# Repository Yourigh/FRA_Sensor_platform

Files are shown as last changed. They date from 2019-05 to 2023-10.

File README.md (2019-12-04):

# FRA Sensor platform
Analog and Digital datalogger with 16 analog channels (16bit) with programmable gain amplifier (auto ranged from 0-256mV to 0-5V).

# Main board picture
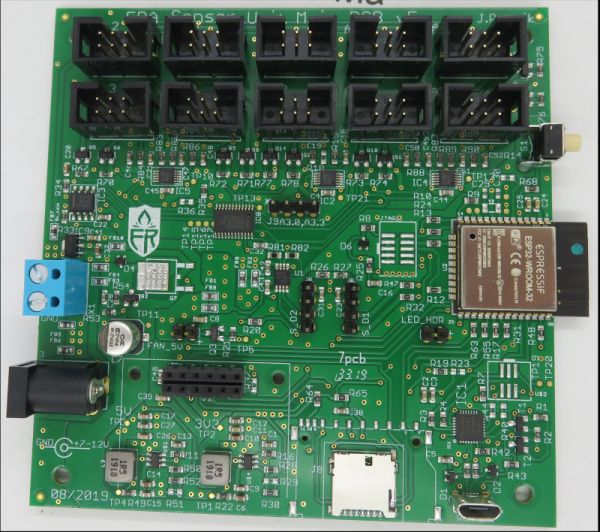
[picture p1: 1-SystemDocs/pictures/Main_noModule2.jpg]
Assembled main board

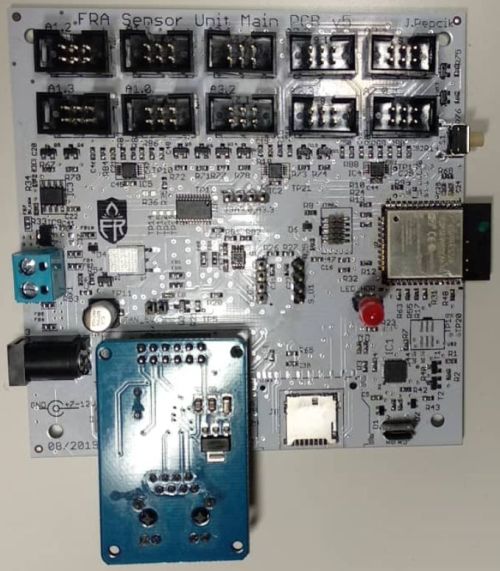
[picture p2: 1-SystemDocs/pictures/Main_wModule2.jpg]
Assembled main board with Ethernet controller


# Development tools
Built on ESP32 module and Arduino framework using Platformio IDE.

# Firmware download to ESP32
https://www.espressif.com/en/products/hardware/esp32/resources

Tools -> Flash Download Tool

Built binary files with the guide are located here:

https://github.com/Yourigh/FRA_Sensor_platform/tree/master/3-FW_SW/1-FW_device/Programming_procedure

Update the esptool.py to newest from:

https://github.com/espressif/esptool

# Resources
https://github.com/greiman/SdFat

https://github.com/jrowberg/i2cdevlib/tree/master/Arduino/ADS1115

https://github.com/8-DK/EtherCard

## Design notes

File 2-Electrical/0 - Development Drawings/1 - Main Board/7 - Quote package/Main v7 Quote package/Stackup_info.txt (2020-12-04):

Board Size: 100x100mm
stackup thickness: 1.6mm
2 layers
single side SMT assembly + single side TH assembly
Legend (silkscreen) - only from TOP side
HAL surface is OK.

Chnage list:
V3.2	original version
V4.1	C19 changed to DNI
V5	D1,D2,D4,D6 package fixed to SC70 (was SOT23)
V7	Changed footprint of ESP32-WROOM-32 to ESP32-WROOM-32E

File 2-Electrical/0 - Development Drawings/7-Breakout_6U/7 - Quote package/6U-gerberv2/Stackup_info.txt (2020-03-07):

Board Size: 51x67mm
stackup thickness: 1.6mm
2 layers
double side TH assembly
HAL surface is OK.

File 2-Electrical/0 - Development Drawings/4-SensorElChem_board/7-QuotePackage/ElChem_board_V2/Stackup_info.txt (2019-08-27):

Board Size: 22x55mm
stackup thickness: 1.6mm
2 layers
single side SMT assembly + single side TH assembly from TOP side
Legend (silkscreen) - both sides

Chnage list:
V1	initial version
V2	Gerber route change (RE and CE on sensor miswired), placment and BOM stays the same

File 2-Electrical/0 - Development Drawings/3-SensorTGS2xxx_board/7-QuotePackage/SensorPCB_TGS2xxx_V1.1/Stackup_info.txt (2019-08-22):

Board Size: 20x30mm
stackup thickness: 1.6mm
2 layers
single side SMT assembly + single side TH assembly from TOP side
Legend (silkscreen) - both sides

Chnage list:
V1	initial version
V1.1	C13 changed from 100n to 1n - only BOM change (affects only variant B)

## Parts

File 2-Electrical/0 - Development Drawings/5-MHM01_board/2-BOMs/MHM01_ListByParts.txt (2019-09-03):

Part	Value	Attributes	Package	Description	Part Num
C1	10u		C1206	CAPACITOR, European symbol	JMF316AB7106KLHT
C2	10u		C1206	CAPACITOR, European symbol	JMF316AB7106KLHT
C3	1u		C0603K	CAPACITOR, European symbol	GRM188R71C105KE15D
C5	10u		C0603K	CAPACITOR, European symbol	GRM188R61A106KE69J
C7	100n		C0603K	CAPACITOR, European symbol	CC0603KRX7R8BB104
FB1			0603	Ferrite Bead	BLM18PG121SN1D
FID1	FIDUCIAL""		FIDUCIAL_1MM	Fiducial Alignment Points	*
FID2	FIDUCIAL""		FIDUCIAL_1MM	Fiducial Alignment Points	*
FID4	FIDUCIAL""		FIDUCIAL_1MM	Fiducial Alignment Points	*
LED2	Red		CHIPLED_1206	LED	BR1101W-TR
PS1	AP2202K-ADJTRG1		SOT95P280X145-5N	DiodesZetex AP2202K-ADJTRG1, Low Noise LDO Voltage Regulator, Adjustable 150mA, 2.3  13.2 V +/-2%, 5-Pin SOT-23	AP2202K-ADJTRG1
Q1	Si2300DS		SOT23	N-Channel Mosfet	JMF316AB7106KLHT
R1	75		R1206	RESISTOR, European symbol	CRCW120675R0FKEA
R2	10k		R0603	RESISTOR, European symbol	CRCW060310K0FKEA
R3	3k		R0603	RESISTOR, European symbol	ERA-3AEB302V
R4	0		R1206	RESISTOR, European symbol	CRCW12060000Z0EA
R7	75		R1206	RESISTOR, European symbol	CRCW120675R0FKEA
R8	10k		R0603	RESISTOR, European symbol	CRCW060310K0FKEA
R9	220		R0603	RESISTOR, European symbol	CRCW0603220RFKEA
R12	100		RJ9W	POTENTIOMETER	3296X-1-101LF
R19	DNI		R1206	RESISTOR, European symbol	*
R20	75		R1206	RESISTOR, European symbol	CRCW120675R0FKEA
R21	75		R1206	RESISTOR, European symbol	CRCW120675R0FKEA
R22	10K		R1206	RESISTOR, European symbol	CRCW120610K0FKEA
TP1	TPTP10R		TP10R	Test pad	*
TP2	TPTP10R		TP10R	Test pad	*
TP6	TPTP10R		TP10R	Test pad	*
TP7	TPTP10R		TP10R	Test pad	*
U$1	CONN_03X2_WE_61200621621		WE_61200621621	https://eu.mouser.com/ProductDetail/Wurth-Elektronik/61200621621?qs=sGAEpiMZZMs%252BGHln7q6pm%2FFhW%252BtWvhAgbNxkR%252BlwXp8Ip%2FAN9J9VOg%3D%3D	61200621621
U2	FIGARO_SR-7		FIGARO-SR7		SR-7
X1	TB001-500-02BE		W237-102	WAGO SCREW CLAMP	TB001-500-02BE
X2	TB001-500-02BE		W237-102	WAGO SCREW CLAMP	TB001-500-02BE
X3	TB001-500-02BE		W237-102	WAGO SCREW CLAMP	TB001-500-02BE

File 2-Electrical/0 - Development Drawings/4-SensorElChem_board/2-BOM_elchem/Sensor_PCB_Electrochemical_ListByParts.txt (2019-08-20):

Part	Value	Attributes	Package	Description	Part Num
C1	DNI		C0603K	CAPACITOR, European symbol	*
C2	100n		C0603K	CAPACITOR, European symbol	GRM188R71C104KA01D
C8	100n		C0603K	CAPACITOR, European symbol	GRM188R71C104KA01D
C9	100n		C0603K	CAPACITOR, European symbol	GRM188R71C104KA01D
C12	100n		C0603K	CAPACITOR, European symbol	GRM188R71C104KA01D
FB9			0603	Ferrite Bead	BLM18PG121SN1D
FID3	FIDUCIAL1X1UNMASKED		FIDUCIAL_1MM_UNMASKED	Fiducial Alignment Points	*
FID5	FIDUCIAL1X1UNMASKED		FIDUCIAL_1MM_UNMASKED	Fiducial Alignment Points	*
FID6	FIDUCIAL1X1UNMASKED		FIDUCIAL_1MM_UNMASKED	Fiducial Alignment Points	*
FID7	FIDUCIAL1X1UNMASKED		FIDUCIAL_1MM_UNMASKED	Fiducial Alignment Points	*
FID8	FIDUCIAL1X1UNMASKED		FIDUCIAL_1MM_UNMASKED	Fiducial Alignment Points	*
FID9	FIDUCIAL1X1UNMASKED		FIDUCIAL_1MM_UNMASKED	Fiducial Alignment Points	*
IC4	LMP91000SD_NOPB		SON50P400X400X80-15N	Configurable AFE Potentiostat for Low-Power Chemical Sensing Applications	LMP91000
IC5	REF3125AQDBZRQ1		SOT95P237X112-3N	Automotive 20-ppm/C (max), 100-A, 3-pin SOT-23 series voltage reference	REF3125AQDBZRQ1
J1	CONN_03X2_WE_61200621621		WE_61200621621	https://eu.mouser.com/ProductDetail/Wurth-Elektronik/61200621621?qs=sGAEpiMZZMs%252BGHln7q6pm%2FFhW%252BtWvhAgbNxkR%252BlwXp8Ip%2FAN9J9VOg%3D%3D	30306-6002HB
J2	2wire		1X02	PIN HEADER	TSW-102-07-G-S
JP2	JUMPER-SMT_3_NO_NO_SILK		SMT-JUMPER_3_0-NO_TRACE_NO-SILK	Normally open jumper	*
LED1			CHIP-LED0603	LED	IN-S63AT5G
Q1	PMBFJ177,215		SOT95P230X110-3N	NXP PMBFJ177,215 P-channel JFET Transistor, 30 V, Idss 1.5  20mA, 3-Pin SOT-23	PMBFJ177,215
R12	10		R0603	RESISTOR, European symbol	CRCW060310R0FKEA
R20	10k		R0603	RESISTOR, European symbol	CRCW060310K0FKEA
R21	10k		R0603	RESISTOR, European symbol	CRCW060310K0FKEA
R22	0		R0603	RESISTOR, European symbol	CRCW06030000Z0EA
R24	100		R0603	RESISTOR, European symbol	CRCW0603100RFKEA
U2	TGS5042		TGS5042	TGS5042	INSTALLED_BY_CUSTOMER
X1	3-ELECTRODE-GAS-SENSOR_SOCKET		3-ELE_SOCKET_ANDON	3 electrode electrochemical sensors	INSTALLED_BY_CUSTOMER

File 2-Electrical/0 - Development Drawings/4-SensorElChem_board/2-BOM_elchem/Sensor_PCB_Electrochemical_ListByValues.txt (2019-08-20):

Qty	Value	Part Num	Package	Parts
1		BLM18PG121SN1D	0603	FB9
1		IN-S63AT5G	CHIP-LED0603	LED1
1	0	CRCW06030000Z0EA	R0603	R22
1	2wire	TSW-102-07-G-S	1X02	J2
1	3-ELECTRODE-GAS-SENSOR_SOCKET	INSTALLED_BY_CUSTOMER	3-ELE_SOCKET_ANDON	X1
1	10	CRCW060310R0FKEA	R0603	R12
2	10k	CRCW060310K0FKEA	R0603	R20, R21
1	100	CRCW0603100RFKEA	R0603	R24
4	100n	GRM188R71C104KA01D	C0603K	C2, C8, C9, C12
1	CONN_03X2_WE_61200621621	30306-6002HB	WE_61200621621	J1
1	DNI	*	C0603K	C1
6	FIDUCIAL1X1UNMASKED	*	FIDUCIAL_1MM_UNMASKED	FID3, FID5, FID6, FID7, FID8, FID9
1	JUMPER-SMT_3_NO_NO_SILK	*	SMT-JUMPER_3_0-NO_TRACE_NO-SILK	JP2
1	LMP91000SD_NOPB	LMP91000	SON50P400X400X80-15N	IC4
1	PMBFJ177,215	PMBFJ177,215	SOT95P230X110-3N	Q1
1	REF3125AQDBZRQ1	REF3125AQDBZRQ1	SOT95P237X112-3N	IC5
1	TGS5042	INSTALLED_BY_CUSTOMER	TGS5042	U2

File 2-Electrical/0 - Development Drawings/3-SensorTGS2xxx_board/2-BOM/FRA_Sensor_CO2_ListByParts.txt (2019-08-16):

Part	Value	Attributes	Package	Description	Part Num
C1(DNP)	100n		C0603K	CAPACITOR, European symbol	GRM188R71C104KA01D
C2	100n		C0603K	CAPACITOR, European symbol	GRM188R71C104KA01D
C3	100n		C0603K	CAPACITOR, European symbol	GRM188R71C104KA01D
C9	100n		C0603K	CAPACITOR, European symbol	GRM188R71H102KA01D
C10(DNP)	1n		C0603K	CAPACITOR, European symbol	GRM188R71H102KA01D
C13(DNP)	100n		C0603K	CAPACITOR, European symbol	GRM188R71C104KA01D
FB1(DNP)			0603	Ferrite Bead	BLM18PG121SN1D
FB9			0603	Ferrite Bead	BLM18PG121SN1D
FID1	FIDUCIAL""		FIDUCIAL_1MM	Fiducial Alignment Points	*
FID2	FIDUCIAL""		FIDUCIAL_1MM	Fiducial Alignment Points	*
FID4	FIDUCIAL""		FIDUCIAL_1MM	Fiducial Alignment Points	*
IC3	LMV796MF_NOPB		SOT95P280X145-5N	Single 17 MHz, low noise, CMOS input, 1.8V operational amplifier	LMV796MF
IC6(DNP)	MCP6541T-I_OT		SOT95P270X145-5N	Comparator Push-Pull RRIO 1.6V SOT23-5	MCP6541T-I/OT
J1	CONN_03X2		WE_61200621621	https://eu.mouser.com/ProductDetail/Wurth-Elektronik/61200621621?qs=sGAEpiMZZMs%252BGHln7q6pm%2FFhW%252BtWvhAgbNxkR%252BlwXp8Ip%2FAN9J9VOg%3D%3D	30306-6002HB
Q3(DNP)	Si2300DS		SOT23	N-Channel Mosfet	SI2300DS-T1-GE3
R1(DNP)	100k		R0603	RESISTOR, European symbol	CRCW0603100KFKEA
R2(DNP)	0		R0603	RESISTOR, European symbol	CRCW06030000Z0EA
R3	0		R0603	RESISTOR, European symbol	CRCW06030000Z0EA
R4	0		R0603	RESISTOR, European symbol	CRCW06035K10FKEA
R10(DNP)	10		R0603	RESISTOR, European symbol	CRCW060310R0FKEA
R11	10		R0603	RESISTOR, European symbol	CRCW060310R0FKEA
R13	0		R0603	RESISTOR, European symbol	CRCW06030000Z0EA
R19	10k		R0603	RESISTOR, European symbol	CRCW060310K0FKEA
R23	0		R0603	RESISTOR, European symbol	CRCW06030000Z0EA
R25(DNP)	100k		R0603	RESISTOR, European symbol	CRCW0603100KFKEA
R26(DNP)	5.1k		R0603	RESISTOR, European symbol	CRCW06035K10FKEA
R27(DNP)	100k		R0603	RESISTOR, European symbol	CRCW0603100KFKEA
U2	FIGARO_SR-7		FIGARO-SR7		INSTALLED_BY_CUSTOMER

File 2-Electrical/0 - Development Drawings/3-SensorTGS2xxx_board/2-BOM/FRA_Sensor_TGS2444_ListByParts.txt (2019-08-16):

Part	Value	Attributes	Package	Description	Part Num
C1(DNP)	100n		C0603K	CAPACITOR, European symbol	GRM188R71C104KA01D
C2	100n		C0603K	CAPACITOR, European symbol	GRM188R71C104KA01D
C3	100n		C0603K	CAPACITOR, European symbol	GRM188R71C104KA01D
C9	1n		C0603K	CAPACITOR, European symbol	GRM188R71H102KA01D
C10	1n		C0603K	CAPACITOR, European symbol	GRM188R71H102KA01D
C13	100n		C0603K	CAPACITOR, European symbol	GRM188R71C104KA01D
FB1			0603	Ferrite Bead	BLM18PG121SN1D
FB9			0603	Ferrite Bead	BLM18PG121SN1D
FID1	FIDUCIAL""		FIDUCIAL_1MM	Fiducial Alignment Points	*
FID2	FIDUCIAL""		FIDUCIAL_1MM	Fiducial Alignment Points	*
FID4	FIDUCIAL""		FIDUCIAL_1MM	Fiducial Alignment Points	*
IC3(DNP)	LMV796MF_NOPB		SOT95P280X145-5N	Single 17 MHz, low noise, CMOS input, 1.8V operational amplifier	LMV796MF
IC6	MCP6541T-I_OT		SOT95P270X145-5N	Comparator Push-Pull RRIO 1.6V SOT23-5	MCP6541T-I/OT
J1	CONN_03X2		WE_61200621621	https://eu.mouser.com/ProductDetail/Wurth-Elektronik/61200621621?qs=sGAEpiMZZMs%252BGHln7q6pm%2FFhW%252BtWvhAgbNxkR%252BlwXp8Ip%2FAN9J9VOg%3D%3D	30306-6002HB
Q3	Si2300DS		SOT23	N-Channel Mosfet	SI2300DS-T1-GE3
R1	100k		R0603	RESISTOR, European symbol	CRCW0603100KFKEA
R2	0		R0603	RESISTOR, European symbol	CRCW06030000Z0EA
R3(DNP)	0		R0603	RESISTOR, European symbol	CRCW06030000Z0EA
R4	5.1k		R0603	RESISTOR, European symbol	CRCW06035K10FKEA
R10	10		R0603	RESISTOR, European symbol	CRCW060310R0FKEA
R11(DNP)	10		R0603	RESISTOR, European symbol	CRCW060310R0FKEA
R13(DNP)	0		R0603	RESISTOR, European symbol	CRCW06030000Z0EA
R19	10k		R0603	RESISTOR, European symbol	CRCW060310K0FKEA
R23(DNP)	0		R0603	RESISTOR, European symbol	CRCW06030000Z0EA
R25	100k		R0603	RESISTOR, European symbol	CRCW0603100KFKEA
R26	5.1k		R0603	RESISTOR, European symbol	CRCW06035K10FKEA
R27	100k		R0603	RESISTOR, European symbol	CRCW0603100KFKEA
U2	FIGARO_SR-7		FIGARO-SR7		INSTALLED_BY_CUSTOMER

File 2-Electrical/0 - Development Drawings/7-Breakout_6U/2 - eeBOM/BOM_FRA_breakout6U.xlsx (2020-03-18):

Qty | Value | MPN | Parts | Mouser
6 | 2x3pin female | SSW-103-01-F-D | U5,U6,U7,U8,U9,U10 | https://www.mouser.com/ProductDetail/Samtec/SSW-103-01-F-D
2 | Terminal 10p vertical | TB003V-500-P10BE | U12,U14 | https://www.mouser.com/ProductDetail/CUI-Devices/TB003V-500-P10BE

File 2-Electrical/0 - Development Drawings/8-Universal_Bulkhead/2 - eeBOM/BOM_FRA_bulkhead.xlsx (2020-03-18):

Qty | Value | MPN | Parts | Mouser
2 | 2pin male | TSW-102-07-G-S | FAN_5V, LED_HDR | https://www.mouser.com/ProductDetail/Samtec/TSW-102-07-G-S
1 | 2pin female | SLW-102-01-T-S | LED_HDR1 | https://www.mouser.com/ProductDetail/Samtec/SLW-102-01-T-S
2 | 4pin male | TSW-104-07-G-S | J9, S_D1 | https://www.mouser.com/ProductDetail/Samtec/TSW-104-07-G-S?qs=sGAEpiMZZMvlX3nhDDO4AAakfwUUEeIPjXtR1hQiW00%3D
2 | 4pin female | SLW-104-01-T-S | S_D2, S_D3 | https://www.mouser.com/ProductDetail/Samtec/SLW-104-01-T-S
20 | 2x3pin male | Wurth 61200621621 | U$1, U$2, U$3, U$4, U$5, U$6, U$8, U$9, U$10, U$11, U$12, U$1 3, U$14, U $15, U$16, U$17, U$18, U$19, U$20, U$21 | https://eu.mouser.com/ProductDetail/Wurth-Elektronik/61200621621
1 | Terminal 2p | TB001-500-02BE | X1 | https://www.mouser.com/ProductDetail/CUI-Devices/TB001-500-02BE
3 | Terminal 5p | TB003-500-P05BE | U1, U3, U22 | https://www.mouser.com/ProductDetail/CUI-Devices/TB003-500-P05BE
2 | Terminal 10p | TB003-500-P10BE | U2, U23 | https://www.mouser.com/ProductDetail/CUI-Devices/TB003-500-P10BE

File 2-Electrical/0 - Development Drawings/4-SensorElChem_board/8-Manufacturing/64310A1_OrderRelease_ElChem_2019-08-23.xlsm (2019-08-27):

 |  |  |  | Production Order Description
 |  |  |  | Number: Q64310A1 |  |  |  |  | Issued by: |  | Eyoel
 |  |  |  |  | 2019-08-23 |  |  |  | Ver: 01
General Information |  |  |  | Project Co-odinator |  |  |  |  | Twinkle
1.Project Name: | ElChem_V1 |  |  |  |  |  |  |  |  | 7.Ordered Date: |  |  | 2019-08-23
2.Gerber received date: | ElChem_V1_2019_08_20 |  |  |  |  |  |  |  |  | 8.Customer ID: |  |  | 52940
3.DFM Check: | Yes |  |  |  |  |  |  |  |  | 9.Repeated order: |  |  | No
4.PCBA Shipment | 1st | 225 | 2nd | 0 | 3rd |  | 4th |  |  | 10.PCBA Ordered: |  |  | 225 | PCS
5.Bare PCB shipmt | 1st | 0 | 2nd | 0 | 3rd |  | 4th |  |  | 11.Customer PO |  |  | 997-007
6.Shipment date: | 2019-09-09 |  |  |  |  |  |  |  |  | 11a. Type of Service |  |  | Turnkey
BOM and Parts Procurement:
12.BOM received Date: | 2019-08-19 |  |  |  |  |  |  |  |  | 15.SZ stock check: |  |  | No
13.Consigned Parts: | None |  |  |  |  |  |  |  |  | 16.Authoriz Code: |  |  | 8279010823
14.DNI Parts: | Item # 3,5,9a,11,12,15,16 |  |  |  |  |  |  |  |  | 17.Parts procurement: |  |  | Geoffrey |  |  | # of days required for Purchasing | 3
17a. Procurement finish Date | 2019-08-26 |  |  |  |  |  |  |  |  | 17b. Parts arrival in Toronto |  |  | 2019-08-27
 |  |  |  |  |  |  |  |  |  |  |  |  |  |  |  | Note: These days are not for rush orders
Special Assembly Requirements: |  |  |  |  |  |  |  |  |  | 18.Assembly Process |  |  | Lead-free
Please process as a rush order as the client has paid extra for it. Please fabricate all the boards by August 30th, parts should arrive by then.
Please assemble as soon as possible and send out by September 9th.
Process In Markham.
19.Returning Parts: | None |  |  | 24.Conformal Coating: |  |  |  | No |  |  | 28.SMT Pads |  | 45
 |  |  |  |  |  |  |  |  |  |  | 29. Holes |  | 10
20.Picture Approval: | Yes |  |  | 25.Programming: |  |  |  | No |  |  | 30. BOM Lines |  | 17
 |  |  |  |  |  |  |  |  |  |  | 31. All Parts |  | 14
21.Functional Testing: | No |  |  | 26.Shipped by: |  |  |  | UPS/FedEx |  |  | 32. Double side |  | N
 |  |  |  |  |  |  |  |  |  |  | 33. Leadfree |  | Y
22.Files Provided: | Gerber files, ProductionBOM |  |  |  |  |  |  |  |  |  | 34. BGA/Fine Pitch |  | 0
 |  |  |  |  |  |  |  |  |  |  | 35. Package |  | 0603
23.Parts for Approval: | None |  |  | 27. Balance Payment: |  |  |  | - |  |  | 37. BGA/QFN |  | 0 | 0 | 0.00
 |  |  |  |  |  |  |  |  |  |  | 38. Fine Pitch |  | 0 | 0 | 0.00
PCB fab notes: |  | 1st order: |  | 225 | PCS |  |  |  | 2nd order: |  | 0 | PCS
Other requirements: Please process as a rush order as the client has paid extra for it. Please fabricate all the boards by August 30th, parts should arrive by then.
Please assemble as soon as possible and send out by September 9th.
Board Size: | 0.86 |  | inch | X | 2.16 | inch |  |  | Impedance Control: |  |  |  | NO
Panel Size: |  |  | inch | X |  | inch |  |  | Materials: |  |  | FR4(TG140)
Board Thickness: | 0.063 |  | inch |  |  |  |  |  | No. of Layers: |  |  | 2
Legend Color: | White |  |  | 2 | Sides |  |  |  | Mask Color: |  |  | Green |  | 2 | Sides
Copper Weight: | Outer 1.0/1.0 oz |  |  |  |  |  |  |  | Electrical Testing: |  |  |  | YES
Panelization: |  |  |  | 1PNL | = |  | pcs. |  | Surface Finish: |  |  | Gold Immersion
Blind or Buried vias: |  | NO |  |  |  |  |  |  | Gold finger: |  |  |  | NO
 |  |  |  |  |  |  |  |  | Via on Pad: |  |  | NO

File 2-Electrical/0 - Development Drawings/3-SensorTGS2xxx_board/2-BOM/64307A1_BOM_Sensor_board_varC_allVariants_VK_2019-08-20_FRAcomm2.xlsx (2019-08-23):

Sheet: varA
Variant A - TGS2xxx
Assembly:
Part | Value | Package | Description | Part Num | X [mm] | Y [mm] | Orientation
C1 | 100n | C0603K | CAPACITOR, European symbol | GRM188R71C104KA01D | 15.355 | 28.544 | R180
C2 | 100n | C0603K | CAPACITOR, European symbol | GRM188R71C104KA01D | 8.385 | 11.022 | R0
FB1 |  | 603 | Ferrite Bead | BLM18PG121SN1D | 11.22 | 17.452 | R180
FB9 |  | 603 | Ferrite Bead | BLM18PG121SN1D | 10.409 | 13.299 | R0
FID1 | FIDUCIAL"" | FIDUCIAL_1MM | Fiducial Alignment Points | * | 14.59 | 1.355 | R0
FID2 | FIDUCIAL"" | FIDUCIAL_1MM | Fiducial Alignment Points | * | 3.11 | 24.92 | R0
FID4 | FIDUCIAL"" | FIDUCIAL_1MM | Fiducial Alignment Points | * | 18.925 | 28.94 | R0
J1 | CONN_03X2 | WE_61200621621 | Pin header connector | 30306-6002HB | 7.136 | 5.278 | R270
R2 | 0 | R0603 | RESISTOR, European symbol | CRCW06030000Z0EA | 10.035 | 24.885 | R90
R4 | 5.1k | R0603 | RESISTOR, European symbol | CRCW06035K10FKEA | 18.535 | 18.734 | R270
R10 | 10 | R0603 | RESISTOR, European symbol | CRCW060310R0FKEA | 18.038 | 6.487 | R270
R23 | 0 | R0603 | RESISTOR, European symbol | CRCW06030000Z0EA | 18.569 | 14.186 | R270
Procurement:
Qty | Value | Part Num | Package | Parts | Alternative
2 |  | BLM18PG121SN1D | 603 | FB1, FB9
2 | 0 | CRCW06030000Z0EA | R0603 | R2, R3(DNP), R13(DNP), R23
0 | 1n | GRM188R71H102KA01D | C0603K | C9(DNP), C10(DNP)
1 | 5.1k | CRCW06035K10FKEA | R0603 | R4, R26(DNP)
1 | 10 | CRCW060310R0FKEA | R0603 | R10, R11(DNP)
0 | 10k | CRCW060310K0FKEA | R0603 | R19(DNP)
0 | 100k | CRCW0603100KFKEA | R0603 | R1(DNP), R25(DNP), R27(DNP)
2 | 100n | GRM188R71C104KA01D | C0603K | C1, C2, C3(DNP), C13(DNP)
1 | CONN_03X2 | 30306-6002HB |  | J1 | Wurth 61200621621
0 | LMV796MF_NOPB | LMV796MF | SOT95P280X145-5N | IC3(DNP)
0 | MCP6541T-I_OT | MCP6541T-I/OT | SOT95P270X145-5N | IC6(DNP)
0 | Si2300DS | SI2300DS-T1-GE3 | SOT23 | Q3(DNP)

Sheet: varB
Variant B - TGS2444
Assembly:
Part | Value | Attributes | Package | Description | Part Num | X [mm] | Y [mm] | Orientation
C2 | 100n |  | C0603K | CAPACITOR, European symbol | GRM188R71C104KA01D | 8.385 | 11.022 | R0
C3 | 100n |  | C0603K | CAPACITOR, European symbol | GRM188R71C104KA01D | 2.115 | 23.265 | R0
C9 | 1n |  | C0603K | CAPACITOR, European symbol | GRM188R71H102KA01D | 12.417 | 11.033 | R180
C10 | 1n |  | C0603K | CAPACITOR, European symbol | GRM188R71H102KA01D | 3.983 | 12.292 | R270
C13 | 100n |  | C0603K | CAPACITOR, European symbol | GRM188R71C104KA01D | 15.75 | 12.555 | R0
FB1 |  |  | 603 | Ferrite Bead | BLM18PG121SN1D | 11.22 | 17.452 | R180
FB9 |  |  | 603 | Ferrite Bead | BLM18PG121SN1D | 10.409 | 13.299 | R0
FID1 | FIDUCIAL"" |  | FIDUCIAL_1MM | Fiducial Alignment Points | * | 14.59 | 1.355 | R0
FID2 | FIDUCIAL"" |  | FIDUCIAL_1MM | Fiducial Alignment Points | * | 3.11 | 24.92 | R0
FID4 | FIDUCIAL"" |  | FIDUCIAL_1MM | Fiducial Alignment Points | * | 18.925 | 28.94 | R0
IC6 | MCP6541T-I_OT |  | SOT95P270X145-5N | Comparator Push-Pull RRIO 1.6V SOT23-5 | MCP6541T-I/OT | 4.277 | 17.317 | R270
J1 | CONN_03X2 |  | WE_61200621621 | https://eu.mouser.com/ProductDetail/Wurth-Elektronik/61200621621 | 30306-6002HB | 7.136 | 5.278 | R270
Q3 | Si2300DS |  | SOT23 | N-Channel Mosfet | SI2300DS-T1-GE3 | 15.754 | 15.895 | R0
R1 | 100k |  | R0603 | RESISTOR, European symbol | CRCW0603100KFKEA | 6.738 | 21.313 | R180
R2 | 0 |  | R0603 | RESISTOR, European symbol | CRCW06030000Z0EA | 10.035 | 24.885 | R90
R4 | 5.1k |  | R0603 | RESISTOR, European symbol | CRCW06035K10FKEA | 18.535 | 18.734 | R270
R10 | 10 |  | R0603 | RESISTOR, European symbol | CRCW060310R0FKEA | 18.038 | 6.487 | R270
R19 | 10k |  | R0603 | RESISTOR, European symbol | CRCW060310K0FKEA | 7.695 | 18.405 | R90
R25 | 100k |  | R0603 | RESISTOR, European symbol | CRCW0603100KFKEA | 1.724 | 12.329 | R90
R26 | 5.1k |  | R0603 | RESISTOR, European symbol | CRCW06035K10FKEA | 1.184 | 17.285 | R90
R27 | 100k |  | R0603 | RESISTOR, European symbol | CRCW0603100KFKEA | 2.076 | 20.731 | R0
Procurement:
Qty | Value | Part Num | Package | Parts | Alternative
2 |  | BLM18PG121SN1D | 603 | FB1, FB9
1 | 0 | CRCW06030000Z0EA | R0603 | R2, R3(DNP), R13(DNP), R23(DNP)
2 | 1n | GRM188R71H102KA01D | C0603K | C9, C10
2 | 5.1k | CRCW06035K10FKEA | R0603 | R4, R26
1 | 10 | CRCW060310R0FKEA | R0603 | R10, R11(DNP)
1 | 10k | CRCW060310K0FKEA | R0603 | R19
3 | 100k | CRCW0603100KFKEA | R0603 | R1, R25, R27
3 | 100n | GRM188R71C104KA01D | C0603K | C1(DNP), C2, C3, C13
1 | CONN_03X2 | 30306-6002HB |  | J1 | Wurth 61200621621
1 | FIGARO_SR-7 | INSTALLED_BY_CUSTOMER | FIGARO-SR7 | U2
0 | LMV796MF_NOPB | LMV796MF | SOT95P280X145-5N | IC3(DNP)
1 | MCP6541T-I_OT | MCP6541T-I/OT | SOT95P270X145-5N | IC6
1 | Si2300DS | SI2300DS-T1-GE3 | SOT23 | Q3

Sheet: varC
Variant C - CO2
Assembly:
Part | Value | Attributes | Package | Description | Part Num | X [mm] | Y [mm] | Orientation
C2 | 100n |  | C0603K | CAPACITOR, European symbol | GRM188R71C104KA01D | 8.385 | 11.022 | R0
C3 | 100n |  | C0603K | CAPACITOR, European symbol | GRM188R71C104KA01D | 2.115 | 23.265 | R0
C9 | 100n |  | C0603K | CAPACITOR, European symbol | GRM188R71C104KA01D | 12.417 | 11.033 | R180
FB9 |  |  | 603 | Ferrite Bead | BLM18PG121SN1D | 10.409 | 13.299 | R0
FID1 | FIDUCIAL"" |  | FIDUCIAL_1MM | Fiducial Alignment Points | * | 14.59 | 1.355 | R0
FID2 | FIDUCIAL"" |  | FIDUCIAL_1MM | Fiducial Alignment Points | * | 3.11 | 24.92 | R0
FID4 | FIDUCIAL"" |  | FIDUCIAL_1MM | Fiducial Alignment Points | * | 18.925 | 28.94 | R0
IC3 | LMV796MF_NOPB |  | SOT95P280X145-5N | Single 17 MHz, low noise, CMOS input, 1.8V operational amplifier | LMV796MF | 6.66 | 26.326 | R270
J1 | CONN_03X2 |  | WE_61200621621 | https://eu.mouser.com/ProductDetail/Wurth-Elektronik/61200621621 | 30306-6002HB | 7.136 | 5.278 | R270
R3 | 0 |  | R0603 | RESISTOR, European symbol | CRCW06030000Z0EA | 10.035 | 21.465 | R270
R4 | 0 |  | R0603 | RESISTOR, European symbol | CRCW06030000Z0EA | 18.535 | 18.734 | R270
R11 | 10 |  | R0603 | RESISTOR, European symbol | CRCW060310R0FKEA | 15.694 | 6.487 | R270
R13 | 0 |  | R0603 | RESISTOR, European symbol | CRCW06030000Z0EA | 11.68 | 28.564 | R0
R19 | 10k |  | R0603 | RESISTOR, European symbol | CRCW060310K0FKEA | 7.695 | 18.405 | R90
R23 | 0 |  | R0603 | RESISTOR, European symbol | CRCW06030000Z0EA | 18.569 | 14.186 | R270
Procurement:
Qty | Value | Part Num | Package | Parts | Alternative
1 |  | BLM18PG121SN1D | 603 | FB1(DNP), FB9
4 | 0 | CRCW06030000Z0EA | R0603 | R2(DNP), R3, R4, R13, R23
0 | 1n | GRM188R71H102KA01D | C0603K | C10(DNP)
0 | 5.1k | CRCW06035K10FKEA | R0603 | R26(DNP)
1 | 10 | CRCW060310R0FKEA | R0603 | R10(DNP), R11
1 | 10k | CRCW060310K0FKEA | R0603 | R19
0 | 100k | CRCW0603100KFKEA | R0603 | R1(DNP), R25(DNP), R27(DNP)
2 | 100n | GRM188R71C104KA01D | C0603K | C1(DNP), C2, C3, C13(DNP)
1 | 100n | GRM188R71H102KA01D | C0603K | C9
1 | CONN_03X2 | 30306-6002HB |  | J1 | Wurth 61200621621
1 | FIGARO_SR-7 | INSTALLED_BY_CUSTOMER | FIGARO-SR7 | U2
1 | LMV796MF_NOPB | LMV796MF | SOT95P280X145-5N | IC3
0 | MCP6541T-I_OT | MCP6541T-I/OT | SOT95P270X145-5N | IC6(DNP)
0 | Si2300DS | SI2300DS-T1-GE3 | SOT23 | Q3(DNP)

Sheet: 64307A1_varC_VK
Item# | Qty | Value | Part Num | Package | Parts | Alternative | Qty'30 | Qty'50 | $30 | $50 | _$30 | _$50 | Available | MOQ | Supplier_VK | Production P/N_VK | Supplier P/N_VK | Production MFG_VK | Production Description_VK | Comments_VK | Your Comments
1 | 1 |  | BLM18PG121SN1D | 603 | FB1(DNP), FB9 |  | 30 | 50 | 0.06840 | 0.05000 | 0.06840 | 0.05000 | 393450 | 1 | Digi-Key | BLM18PG121SN1D | 490-1037-1-ND | Murata Manufacturing Co Ltd | FERRITE BEAD 120 OHM 0603 1LN
2 | 4 | 0 | CRCW06030000Z0EA | R0603 | R2(DNP), R3, R4, R13, R23 |  | 120 | 200 |  |  | 0.00000 | 0.00000 | 952006 | 1 | Bittele | CRCW06030000Z0EA |  | Vishay Dale | RES SMD 0.0OHM JUMPER 1/10W 0603 | "Bittele Stock" | approved
3 | 0 | 1n | GRM188R71H102KA01D | C0603K | C10(DNP) |  | 0 | 0 |  |  | 0.00000 | 0.00000 |  | 1 |  |  |  |  |  | "DO NOT INSTALL" | approved
4 | 0 | 5.1k | CRCW06035K10FKEA | R0603 | R26(DNP) |  | 0 | 0 |  |  | 0.00000 | 0.00000 |  | 1 |  |  |  |  |  | "DO NOT INSTALL" | approved
5 | 1 | 10 | CRCW060310R0FKEA | R0603 | R10(DNP), R11 |  | 30 | 50 |  |  | 0.00000 | 0.00000 | 140573 | 1 | Bittele | CRCW060310R0FKEA |  | Vishay Dale | RES SMD 10 OHM 1% 1/10W 0603 | "Bittele Stock" | approved
6 | 1 | 10k | CRCW060310K0FKEA | R0603 | R19 |  | 30 | 50 |  |  | 0.00000 | 0.00000 | 1896080 | 1 | Bittele | CRCW060310K0FKEA |  | Vishay Dale | RES SMD 10K OHM 1% 1/10W 0603 | "Bittele Stock" | approved
7 | 0 | 100k | CRCW0603100KFKEA | R0603 | R1(DNP), R25(DNP), R27(DNP) |  | 0 | 0 |  |  | 0.00000 | 0.00000 |  | 1 |  |  |  |  |  | "DO NOT INSTALL" | approved
8 | 2 | 100n | GRM188R71C104KA01D | C0603K | C1(DNP), C2, C3, C13(DNP) |  | 60 | 100 | 0.11500 | 0.05400 | 0.23000 | 0.10800 | 2405151 | 1 | Digi-Key | 0603YC104KAT2A | 478-1239-1-ND | AVX Corporation | CAP CER 0.1UF 16V X7R 0603 | Please confirm the "Mfg P/N:0603YC104KAT2A". | approved
9 | 1 | 100n | GRM188R71H102KA01D | C0603K | C9 |  | 30 | 50 | 0.08800 | 0.08800 | 0.08800 | 0.08800 | 1098930 | 1 | Digi-Key | C0603C102K5RACTU | 399-1082-1-ND | KEMET Corporation | CAP CER 1000PF 50V X7R 0603 | Please confirm the "Mfg P/N:C0603C102K5RACTU". & The description in column"C" refers to "100nF" whereas online description refers to "1000PF".Please comment. | my mistake, should be 100n, same as previous row
10 | 1 | CONN_03X2 | 30306-6002HB |  | J1 | Wurth 61200621621 | 30 | 50 | 0.63000 | 0.63000 | 0.63000 | 0.63000 | 2296 | 1 | Digi-Key | 30306-6002HB | 3M15451-ND | 3M Interconnect | CONN HEADER VERT 6POS 2.54MM
11 | 1 | FIGARO_SR-7 | INSTALLED_BY_CUSTOMER | FIGARO-SR7 | U2 |  | 30 | 50 |  |  | 0.00000 | 0.00000 |  | 1 |  |  |  |  |  | "Consigned Part" | Do not install
12 | 1 | LMV796MF_NOPB | LMV796MF | SOT95P280X145-5N | IC3 |  | 30 | 50 | 1.26000 | 1.26000 | 1.26000 | 1.26000 | 3542 | 1 | Mouser | LMV796MF/NOPB | 926-LMV796MF/NOPB | Texas Instruments | Operational Amplifiers - Op Amps 17MHz Lo Noise CMOS Input 1.8V OP Amps | Please confirm the "Mfg P/N:LMV796MF/NOPB". | approved
13 | 0 | MCP6541T-I_OT | MCP6541T-I/OT | SOT95P270X145-5N | IC6(DNP) |  | 0 | 0 |  |  | 0.00000 | 0.00000 |  | 1 |  |  |  |  |  | "DO NOT INSTALL" | approved
14 | 0 | Si2300DS | SI2300DS-T1-GE3 | SOT23 | Q3(DNP) |  | 0 | 0 |  |  | 0.00000 | 0.00000 |  | 1 |  |  |  |  |  | "DO NOT INSTALL" | approved
 |  |  |  |  |  |  |  |  | Sub-Total |  | 2.27640 | 2.13600
 |  |  |  |  |  |  |  |  | Production Loss |  | 0.09106 | 0.08544
 |  |  |  |  |  |  |  |  | Supplier Shipping Cost |  | 0.00000 | 0.00000
 |  |  |  |  |  |  |  |  | PARTS TOTAL |  | 2.36746 | 2.22144

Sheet: 64307A1_varC_VK_0822
Item# | Qty | Value | Part Num | Package | Parts | Alternative | Qty'30 | Qty'50 | $30 | $50 | _$30 | _$50 | Available | MOQ | Supplier_VK | Production P/N_VK | Supplier P/N_VK | Production MFG_VK | Production Description_VK | Comments_VK | Your Comments
1 | 1 |  | BLM18PG121SN1D | 603 | FB1(DNP), FB9 |  | 30 | 50 | 0.06840 | 0.05000 | 0.06840 | 0.05000 | 393450 | 1 | Digi-Key | BLM18PG121SN1D | 490-1037-1-ND | Murata Manufacturing Co Ltd | FERRITE BEAD 120 OHM 0603 1LN
2 | 4 | 0 | CRCW06030000Z0EA | R0603 | R2(DNP), R3, R4, R13, R23 |  | 120 | 200 |  |  | 0.00000 | 0.00000 | 952006 | 1 | Bittele | CRCW06030000Z0EA |  | Vishay Dale | RES SMD 0.0OHM JUMPER 1/10W 0603 | "Bittele Stock" | approved
3 | 0 | 1n | GRM188R71H102KA01D | C0603K | C10(DNP) |  | 0 | 0 |  |  | 0.00000 | 0.00000 |  | 1 |  |  |  |  |  | "DO NOT INSTALL" | approved
4 | 0 | 5.1k | CRCW06035K10FKEA | R0603 | R26(DNP) |  | 0 | 0 |  |  | 0.00000 | 0.00000 |  | 1 |  |  |  |  |  | "DO NOT INSTALL" | approved
5 | 1 | 10 | CRCW060310R0FKEA | R0603 | R10(DNP), R11 |  | 30 | 50 |  |  | 0.00000 | 0.00000 | 140573 | 1 | Bittele | CRCW060310R0FKEA |  | Vishay Dale | RES SMD 10 OHM 1% 1/10W 0603 | "Bittele Stock" | approved
6 | 1 | 10k | CRCW060310K0FKEA | R0603 | R19 |  | 30 | 50 |  |  | 0.00000 | 0.00000 | 1896080 | 1 | Bittele | CRCW060310K0FKEA |  | Vishay Dale | RES SMD 10K OHM 1% 1/10W 0603 | "Bittele Stock" | approved
7 | 0 | 100k | CRCW0603100KFKEA | R0603 | R1(DNP), R25(DNP), R27(DNP) |  | 0 | 0 |  |  | 0.00000 | 0.00000 |  | 1 |  |  |  |  |  | "DO NOT INSTALL" | approved
8 | 2 | 100n | GRM188R71C104KA01D | C0603K | C1(DNP), C2, C3, C13(DNP) |  | 60 | 100 | 0.11500 | 0.05400 | 0.23000 | 0.10800 | 2405151 | 1 | Digi-Key | 0603YC104KAT2A | 478-1239-1-ND | AVX Corporation | CAP CER 0.1UF 16V X7R 0603 |  | approved
9 | 1 | 100n | GRM188R71H102KA01D | C0603K | C9 |  | 30 | 50 | 0.11500 | 0.11500 | 0.11500 | 0.11500 | 2405151 | 1 | Digi-Key | 0603YC104KAT2A | 478-1239-1-ND | AVX Corporation | CAP CER 0.1UF 16V X7R 0603 | The part is now the same as the one above. | my mistake, should be 100n, same as previous row
10 | 1 | CONN_03X2 | 30306-6002HB |  | J1 | Wurth 61200621621 | 30 | 50 | 0.63000 | 0.63000 | 0.63000 | 0.63000 | 2296 | 1 | Digi-Key | 30306-6002HB | 3M15451-ND | 3M Interconnect | CONN HEADER VERT 6POS 2.54MM
11 | 1 | FIGARO_SR-7 | INSTALLED_BY_CUSTOMER | FIGARO-SR7 | U2 |  | 30 | 50 |  |  | 0.00000 | 0.00000 |  | 1 |  |  |  |  |  | "Consigned Part" | Do not install
12 | 1 | LMV796MF_NOPB | LMV796MF | SOT95P280X145-5N | IC3 |  | 30 | 50 | 1.26000 | 1.26000 | 1.26000 | 1.26000 | 3542 | 1 | Mouser | LMV796MF/NOPB | 926-LMV796MF/NOPB | Texas Instruments | Operational Amplifiers - Op Amps 17MHz Lo Noise CMOS Input 1.8V OP Amps | Please confirm the "Mfg P/N:LMV796MF/NOPB". | approved
13 | 0 | MCP6541T-I_OT | MCP6541T-I/OT | SOT95P270X145-5N | IC6(DNP) |  | 0 | 0 |  |  | 0.00000 | 0.00000 |  | 1 |  |  |  |  |  | "DO NOT INSTALL" | approved
14 | 0 | Si2300DS | SI2300DS-T1-GE3 | SOT23 | Q3(DNP) |  | 0 | 0 |  |  | 0.00000 | 0.00000 |  | 1 |  |  |  |  |  | "DO NOT INSTALL" | approved
 |  |  |  |  |  |  |  |  | Sub-Total |  | 2.30340 | 2.16300
 |  |  |  |  |  |  |  |  | Production Loss |  | 0.09214 | 0.08652
 |  |  |  |  |  |  |  |  | Supplier Shipping Cost |  | 0.00000 | 0.00000
 |  |  |  |  |  |  |  |  | PARTS TOTAL |  | 2.39554 | 2.24952

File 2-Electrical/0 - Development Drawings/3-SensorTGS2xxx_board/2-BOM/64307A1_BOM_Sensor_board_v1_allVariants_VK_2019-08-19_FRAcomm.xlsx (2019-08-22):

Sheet: varA
Variant A - TGS2xxx
Assembly:
Part | Value | Package | Description | Part Num | X [mm] | Y [mm] | Orientation
C1 | 100n | C0603K | CAPACITOR, European symbol | GRM188R71C104KA01D | 15.355 | 28.544 | R180
C2 | 100n | C0603K | CAPACITOR, European symbol | GRM188R71C104KA01D | 8.385 | 11.022 | R0
FB1 |  | 603 | Ferrite Bead | BLM18PG121SN1D | 11.22 | 17.452 | R180
FB9 |  | 603 | Ferrite Bead | BLM18PG121SN1D | 10.409 | 13.299 | R0
FID1 | FIDUCIAL"" | FIDUCIAL_1MM | Fiducial Alignment Points | * | 14.59 | 1.355 | R0
FID2 | FIDUCIAL"" | FIDUCIAL_1MM | Fiducial Alignment Points | * | 3.11 | 24.92 | R0
FID4 | FIDUCIAL"" | FIDUCIAL_1MM | Fiducial Alignment Points | * | 18.925 | 28.94 | R0
J1 | CONN_03X2 | WE_61200621621 | Pin header connector | 30306-6002HB | 7.136 | 5.278 | R270
R2 | 0 | R0603 | RESISTOR, European symbol | CRCW06030000Z0EA | 10.035 | 24.885 | R90
R4 | 5.1k | R0603 | RESISTOR, European symbol | CRCW06035K10FKEA | 18.535 | 18.734 | R270
R10 | 10 | R0603 | RESISTOR, European symbol | CRCW060310R0FKEA | 18.038 | 6.487 | R270
R23 | 0 | R0603 | RESISTOR, European symbol | CRCW06030000Z0EA | 18.569 | 14.186 | R270
Procurement:
Qty | Value | Part Num | Package | Parts | Alternative
2 |  | BLM18PG121SN1D | 603 | FB1, FB9
2 | 0 | CRCW06030000Z0EA | R0603 | R2, R3(DNP), R13(DNP), R23
0 | 1n | GRM188R71H102KA01D | C0603K | C9(DNP), C10(DNP)
1 | 5.1k | CRCW06035K10FKEA | R0603 | R4, R26(DNP)
1 | 10 | CRCW060310R0FKEA | R0603 | R10, R11(DNP)
0 | 10k | CRCW060310K0FKEA | R0603 | R19(DNP)
0 | 100k | CRCW0603100KFKEA | R0603 | R1(DNP), R25(DNP), R27(DNP)
2 | 100n | GRM188R71C104KA01D | C0603K | C1, C2, C3(DNP), C13(DNP)
1 | CONN_03X2 | 30306-6002HB |  | J1 | Wurth 61200621621
0 | LMV796MF_NOPB | LMV796MF | SOT95P280X145-5N | IC3(DNP)
0 | MCP6541T-I_OT | MCP6541T-I/OT | SOT95P270X145-5N | IC6(DNP)
0 | Si2300DS | SI2300DS-T1-GE3 | SOT23 | Q3(DNP)

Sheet: varB
Variant B - TGS2444
Assembly:
Part | Value | Attributes | Package | Description | Part Num | X [mm] | Y [mm] | Orientation
C2 | 100n |  | C0603K | CAPACITOR, European symbol | GRM188R71C104KA01D | 8.385 | 11.022 | R0
C3 | 100n |  | C0603K | CAPACITOR, European symbol | GRM188R71C104KA01D | 2.115 | 23.265 | R0
C9 | 1n |  | C0603K | CAPACITOR, European symbol | GRM188R71H102KA01D | 12.417 | 11.033 | R180
C10 | 1n |  | C0603K | CAPACITOR, European symbol | GRM188R71H102KA01D | 3.983 | 12.292 | R270
C13 | 100n |  | C0603K | CAPACITOR, European symbol | GRM188R71C104KA01D | 15.75 | 12.555 | R0
FB1 |  |  | 603 | Ferrite Bead | BLM18PG121SN1D | 11.22 | 17.452 | R180
FB9 |  |  | 603 | Ferrite Bead | BLM18PG121SN1D | 10.409 | 13.299 | R0
FID1 | FIDUCIAL"" |  | FIDUCIAL_1MM | Fiducial Alignment Points | * | 14.59 | 1.355 | R0
FID2 | FIDUCIAL"" |  | FIDUCIAL_1MM | Fiducial Alignment Points | * | 3.11 | 24.92 | R0
FID4 | FIDUCIAL"" |  | FIDUCIAL_1MM | Fiducial Alignment Points | * | 18.925 | 28.94 | R0
IC6 | MCP6541T-I_OT |  | SOT95P270X145-5N | Comparator Push-Pull RRIO 1.6V SOT23-5 | MCP6541T-I/OT | 4.277 | 17.317 | R270
J1 | CONN_03X2 |  | WE_61200621621 | https://eu.mouser.com/ProductDetail/Wurth-Elektronik/61200621621 | 30306-6002HB | 7.136 | 5.278 | R270
Q3 | Si2300DS |  | SOT23 | N-Channel Mosfet | SI2300DS-T1-GE3 | 15.754 | 15.895 | R0
R1 | 100k |  | R0603 | RESISTOR, European symbol | CRCW0603100KFKEA | 6.738 | 21.313 | R180
R2 | 0 |  | R0603 | RESISTOR, European symbol | CRCW06030000Z0EA | 10.035 | 24.885 | R90
R4 | 5.1k |  | R0603 | RESISTOR, European symbol | CRCW06035K10FKEA | 18.535 | 18.734 | R270
R10 | 10 |  | R0603 | RESISTOR, European symbol | CRCW060310R0FKEA | 18.038 | 6.487 | R270
R19 | 10k |  | R0603 | RESISTOR, European symbol | CRCW060310K0FKEA | 7.695 | 18.405 | R90
R25 | 100k |  | R0603 | RESISTOR, European symbol | CRCW0603100KFKEA | 1.724 | 12.329 | R90
R26 | 5.1k |  | R0603 | RESISTOR, European symbol | CRCW06035K10FKEA | 1.184 | 17.285 | R90
R27 | 100k |  | R0603 | RESISTOR, European symbol | CRCW0603100KFKEA | 2.076 | 20.731 | R0
Procurement:
Qty | Value | Part Num | Package | Parts | Alternative
2 |  | BLM18PG121SN1D | 603 | FB1, FB9
1 | 0 | CRCW06030000Z0EA | R0603 | R2, R3(DNP), R13(DNP), R23(DNP)
2 | 1n | GRM188R71H102KA01D | C0603K | C9, C10
2 | 5.1k | CRCW06035K10FKEA | R0603 | R4, R26
1 | 10 | CRCW060310R0FKEA | R0603 | R10, R11(DNP)
1 | 10k | CRCW060310K0FKEA | R0603 | R19
3 | 100k | CRCW0603100KFKEA | R0603 | R1, R25, R27
3 | 100n | GRM188R71C104KA01D | C0603K | C1(DNP), C2, C3, C13
1 | CONN_03X2 | 30306-6002HB |  | J1 | Wurth 61200621621
1 | FIGARO_SR-7 | INSTALLED_BY_CUSTOMER | FIGARO-SR7 | U2
0 | LMV796MF_NOPB | LMV796MF | SOT95P280X145-5N | IC3(DNP)
1 | MCP6541T-I_OT | MCP6541T-I/OT | SOT95P270X145-5N | IC6
1 | Si2300DS | SI2300DS-T1-GE3 | SOT23 | Q3

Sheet: varC
Variant C - CO2
Assembly:
Part | Value | Attributes | Package | Description | Part Num | X [mm] | Y [mm] | Orientation
C2 | 100n |  | C0603K | CAPACITOR, European symbol | GRM188R71C104KA01D | 8.385 | 11.022 | R0
C3 | 100n |  | C0603K | CAPACITOR, European symbol | GRM188R71C104KA01D | 2.115 | 23.265 | R0
C9 | 100n |  | C0603K | CAPACITOR, European symbol | GRM188R71C104KA01D | 12.417 | 11.033 | R180
FB9 |  |  | 603 | Ferrite Bead | BLM18PG121SN1D | 10.409 | 13.299 | R0
FID1 | FIDUCIAL"" |  | FIDUCIAL_1MM | Fiducial Alignment Points | * | 14.59 | 1.355 | R0
FID2 | FIDUCIAL"" |  | FIDUCIAL_1MM | Fiducial Alignment Points | * | 3.11 | 24.92 | R0
FID4 | FIDUCIAL"" |  | FIDUCIAL_1MM | Fiducial Alignment Points | * | 18.925 | 28.94 | R0
IC3 | LMV796MF_NOPB |  | SOT95P280X145-5N | Single 17 MHz, low noise, CMOS input, 1.8V operational amplifier | LMV796MF | 6.66 | 26.326 | R270
J1 | CONN_03X2 |  | WE_61200621621 | https://eu.mouser.com/ProductDetail/Wurth-Elektronik/61200621621 | 30306-6002HB | 7.136 | 5.278 | R270
R3 | 0 |  | R0603 | RESISTOR, European symbol | CRCW06030000Z0EA | 10.035 | 21.465 | R270
R4 | 0 |  | R0603 | RESISTOR, European symbol | CRCW06030000Z0EA | 18.535 | 18.734 | R270
R11 | 10 |  | R0603 | RESISTOR, European symbol | CRCW060310R0FKEA | 15.694 | 6.487 | R270
R13 | 0 |  | R0603 | RESISTOR, European symbol | CRCW06030000Z0EA | 11.68 | 28.564 | R0
R19 | 10k |  | R0603 | RESISTOR, European symbol | CRCW060310K0FKEA | 7.695 | 18.405 | R90
R23 | 0 |  | R0603 | RESISTOR, European symbol | CRCW06030000Z0EA | 18.569 | 14.186 | R270
Procurement:
Qty | Value | Part Num | Package | Parts | Alternative
1 |  | BLM18PG121SN1D | 603 | FB1(DNP), FB9
4 | 0 | CRCW06030000Z0EA | R0603 | R2(DNP), R3, R4, R13, R23
0 | 1n | GRM188R71H102KA01D | C0603K | C10(DNP)
0 | 5.1k | CRCW06035K10FKEA | R0603 | R26(DNP)
1 | 10 | CRCW060310R0FKEA | R0603 | R10(DNP), R11
1 | 10k | CRCW060310K0FKEA | R0603 | R19
0 | 100k | CRCW0603100KFKEA | R0603 | R1(DNP), R25(DNP), R27(DNP)
2 | 100n | GRM188R71C104KA01D | C0603K | C1(DNP), C2, C3, C13(DNP)
1 | 100n | GRM188R71H102KA01D | C0603K | C9
1 | CONN_03X2 | 30306-6002HB |  | J1 | Wurth 61200621621
1 | FIGARO_SR-7 | INSTALLED_BY_CUSTOMER | FIGARO-SR7 | U2
1 | LMV796MF_NOPB | LMV796MF | SOT95P280X145-5N | IC3
0 | MCP6541T-I_OT | MCP6541T-I/OT | SOT95P270X145-5N | IC6(DNP)
0 | Si2300DS | SI2300DS-T1-GE3 | SOT23 | Q3(DNP)

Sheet: Sheet1
Item# | Qty_VK | Part | Value | Package | Description | Part Num | X [mm] | Y [mm] | Orientation | Alternative | Qty'30 | Qty'50 | $30 | $50 | Available | MOQ | Supplier_VK | Production P/N_VK | Production MFG_VK | Production Description_VK | Comments_VK | Your Comments
1 | 1 | C1 | 100n | C0603K | CAPACITOR, European symbol | GRM188R71C104KA01D | 15.355 | 28.544 | R180 |  | 30 | 50 | 0.115 | 0.115 | 2406531 | 1 | Digi-Key | 0603YC104KAT2ADISTI #478-1239-1-ND (https://analytics.supplyframe.com/trackingservlet/track/) | AVX Corporation | CAP CER 0.1UF 16V X7R 0603 | pls
2 | 1 | C2 | 100n | C0603K | CAPACITOR, European symbol | GRM188R71C104KA01D | 8.385 | 11.022 | R0 |  | 30 | 50 |  |  |  | 1
3 | 1 | FB1 |  | 603 | Ferrite Bead | BLM18PG121SN1D | 11.22 | 17.452 | R180 |  | 30 | 50 |  |  |  | 1
4 | 1 | FB9 |  | 603 | Ferrite Bead | BLM18PG121SN1D | 10.409 | 13.299 | R0 |  | 30 | 50 |  |  |  | 1
5 | 1 | FID1 | FIDUCIAL"" | FIDUCIAL_1MM | Fiducial Alignment Points | * | 14.59 | 1.355 | R0 |  | 30 | 50 |  |  |  | 1
6 | 1 | FID2 | FIDUCIAL"" | FIDUCIAL_1MM | Fiducial Alignment Points | * | 3.11 | 24.92 | R0 |  | 30 | 50 |  |  |  | 1
7 | 1 | FID4 | FIDUCIAL"" | FIDUCIAL_1MM | Fiducial Alignment Points | * | 18.925 | 28.94 | R0 |  | 30 | 50 |  |  |  | 1
8 | 1 | J1 | CONN_03X2 | WE_61200621621 | Pin header connector | 30306-6002HB | 7.136 | 5.278 | R270 |  | 30 | 50 |  |  |  | 1
9 | 1 | R2 | 0 | R0603 | RESISTOR, European symbol | CRCW06030000Z0EA | 10.035 | 24.885 | R90 |  | 30 | 50 |  |  |  | 1
10 | 1 | R4 | 5.1k | R0603 | RESISTOR, European symbol | CRCW06035K10FKEA | 18.535 | 18.734 | R270 |  | 30 | 50 |  |  |  | 1
11 | 1 | R10 | 10 | R0603 | RESISTOR, European symbol | CRCW060310R0FKEA | 18.038 | 6.487 | R270 |  | 30 | 50 |  |  |  | 1
12 | 1 | R23 | 0 | R0603 | RESISTOR, European symbol | CRCW06030000Z0EA | 18.569 | 14.186 | R270 |  | 30 | 50 |  |  |  | 1
13 | 2 | FB1, FB9 |  | 603 |  | BLM18PG121SN1D |  |  |  |  | 60 | 100 |  |  |  | 1
14 | 2 | R2, R3(DNP), R13(DNP), R23 | 0 | R0603 |  | CRCW06030000Z0EA |  |  |  |  | 60 | 100 |  |  |  | 1
15 | 0 | C9(DNP), C10(DNP) | 1n | C0603K |  | GRM188R71H102KA01D |  |  |  |  | 0 | 0 |  |  |  | 1
16 | 1 | R4, R26(DNP) | 5.1k | R0603 |  | CRCW06035K10FKEA |  |  |  |  | 30 | 50 |  |  |  | 1
17 | 1 | R10, R11(DNP) | 10 | R0603 |  | CRCW060310R0FKEA |  |  |  |  | 30 | 50 |  |  |  | 1
18 | 0 | R19(DNP) | 10k | R0603 |  | CRCW060310K0FKEA |  |  |  |  | 0 | 0 |  |  |  | 1
19 | 0 | R1(DNP), R25(DNP), R27(DNP) | 100k | R0603 |  | CRCW0603100KFKEA |  |  |  |  | 0 | 0 |  |  |  | 1
20 | 2 | C1, C2, C3(DNP), C13(DNP) | 100n | C0603K |  | GRM188R71C104KA01D |  |  |  |  | 60 | 100 |  |  |  | 1
21 | 1 | J1 | CONN_03X2 |  |  | 30306-6002HB |  |  |  | Wurth 61200621621 | 30 | 50 |  |  |  | 1
22 | 0 | IC3(DNP) | LMV796MF_NOPB | SOT95P280X145-5N |  | LMV796MF |  |  |  |  | 0 | 0 |  |  |  | 1
23 | 0 | IC6(DNP) | MCP6541T-I_OT | SOT95P270X145-5N |  | MCP6541T-I/OT |  |  |  |  | 0 | 0 |  |  |  | 1
24 | 0 | Q3(DNP) | Si2300DS | SOT23 |  | SI2300DS-T1-GE3 |  |  |  |  | 0 | 0 |  |  |  | 1

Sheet: 64307A1_varA_VK
Item# | Qty | Value | Part Num | Package | Parts | Alternative | Qty'30 | Qty'50 | $30 | $50 | _$30 | _$50 | Available | MOQ | Supplier_VK | Production P/N_VK | Supplier P/N_VK | Production MFG_VK | Production Description_VK | Comments_VK | Your Comments
1 | 2 |  | BLM18PG121SN1D | 603 | FB1, FB9 |  | 60 | 100 | 0.05000 | 0.04330 | 0.10000 | 0.08660 | 399610 | 1 | Digi-Key | BLM18PG121SN1D | 490-1037-1-ND | Murata Manufacturing Co Ltd | FERRITE BEAD 120 OHM 0603 1LN
2 | 2 | 0 | CRCW06030000Z0EA | R0603 | R2, R3(DNP), R13(DNP), R23 |  | 60 | 100 |  |  | 0.00000 | 0.00000 | 965044 | 1 | Bittele | CRCW06030000Z0EA |  | Vishay Dale | RES SMD 0.0OHM JUMPER 1/10W 0603 | "Bittele stock" | approved
3 | 0 | 1n | GRM188R71H102KA01D | C0603K | C9(DNP), C10(DNP) |  | 0 | 0 |  |  | 0.00000 | 0.00000 |  | 1 |  |  |  |  |  | "DO NOT INSTALL" | approved
4 | 1 | 5.1k | CRCW06035K10FKEA | R0603 | R4, R26(DNP) |  | 30 | 50 |  |  | 0.00000 | 0.00000 | 225650 | 1 | Bittele | CRCW06035K10FKEA |  | Vishay Dale | RES SMD 5.1K OHM 1% 1/10W 0603 | "Bittele stock" | approved
5 | 1 | 10 | CRCW060310R0FKEA | R0603 | R10, R11(DNP) |  | 30 | 50 |  |  | 0.00000 | 0.00000 | 141605 | 1 | Bittele | CRCW060310R0FKEA |  | Vishay Dale | RES SMD 10 OHM 1% 1/10W 0603 | "Bittele stock" | approved
6 | 0 | 10k | CRCW060310K0FKEA | R0603 | R19(DNP) |  | 0 | 0 |  |  | 0.00000 | 0.00000 |  | 1 |  |  |  |  |  | "DO NOT INSTALL" | approved
7 | 0 | 100k | CRCW0603100KFKEA | R0603 | R1(DNP), R25(DNP), R27(DNP) |  | 0 | 0 |  |  | 0.00000 | 0.00000 |  | 1 |  |  |  |  |  | "DO NOT INSTALL" | approved
8 | 2 | 100n | GRM188R71C104KA01D | C0603K | C1, C2, C3(DNP), C13(DNP) |  | 60 | 100 | 0.11500 | 0.05400 | 0.23000 | 0.10800 | 2406531 | 1 | Digi-Key | 0603YC104KAT2A | 478-1239-1-ND | AVX Corporation | CAP CER 0.1UF 16V X7R 0603 | Please confirm the "Mfg P/N:0603YC104KAT2A". | approved, can be used as alternative
9 | 1 | CONN_03X2 | 30306-6002HB |  | J1 | Wurth 61200621621 | 30 | 50 | 0.63000 | 0.63000 | 0.63000 | 0.63000 | 2296 | 1 | Digi-Key | 30306-6002HB | 3M15451-ND | 3M Interconnect | CONN HEADER VERT 6POS 2.54MM
10 | 0 | LMV796MF_NOPB | LMV796MF | SOT95P280X145-5N | IC3(DNP) |  | 0 | 0 |  |  | 0.00000 | 0.00000 |  | 1 |  |  |  |  |  | "DO NOT INSTALL" | approved
11 | 0 | MCP6541T-I_OT | MCP6541T-I/OT | SOT95P270X145-5N | IC6(DNP) |  | 0 | 0 |  |  | 0.00000 | 0.00000 |  | 1 |  |  |  |  |  | "DO NOT INSTALL" | approved
12 | 0 | Si2300DS | SI2300DS-T1-GE3 | SOT23 | Q3(DNP) |  | 0 | 0 |  |  | 0.00000 | 0.00000 |  | 1 |  |  |  |  |  | "DO NOT INSTALL" | approved
 |  |  |  |  |  |  |  |  | Sub-Total |  | 0.96000 | 0.82460
 |  |  |  |  |  |  |  |  | Production Loss |  | 0.03840 | 0.03298
 |  |  |  |  |  |  |  |  | Supplier Shipping Cost |  | 0.00000 | 0.00000
 |  |  |  |  |  |  |  |  | PARTS TOTAL |  | 0.99840 | 0.85758

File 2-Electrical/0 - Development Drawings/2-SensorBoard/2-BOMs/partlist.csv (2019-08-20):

Partlist
Exported from FRA_daughter_v2.sch at 08-Aug-19 22:05
EAGLE Version 7.6.0 Copyright (c) 1988-2016 CadSoft
Assembly variant:
Part     Value                     Device                    Package              Library        Sheet
C1       1n                        C-EUC0603K                C0603K               resistor       1
C2       100n                      C-EUC0603K                C0603K               resistor       1
C3       1u                        C-EUC0603K                C0603K               resistor       1
C5       10u                       C-EUC0603K                C0603K               resistor       1
C6       DNI                       C-EUC0603K                C0603K               resistor       1
C7       100n                      C-EUC0603K                C0603K               resistor       1
C8       100n                      C-EUC0603K                C0603K               resistor       1
C9       100n                      C-EUC0603K                C0603K               resistor       1
C10      1n                        C-EUC0603K                C0603K               resistor       1
C11      100n                      C-EUC0603K                C0603K               resistor       1
C12      100n                      C-EUC0603K                C0603K               resistor       1
C13      100n                      C-EUC0603K                C0603K               resistor       1
FB1                                FERRITE                   0603                 microbuilder   1
FB9                                FERRITE                   0603                 microbuilder   1
IC1      LMV611                    OPA333DCK                 SC70-5L              linear         1
IC3      LMV796MF_NOPB             LMV796MF_NOPB             SOT95P280X145-5N     SamacSys_Parts 1
IC4      LMP91000SD_NOPB           LMP91000SD_NOPB           SON50P400X400X80-15N SamacSys_Parts 1
IC5      REF3125AQDBZRQ1           REF3125AQDBZRQ1           SOT95P237X112-3N     SamacSys_Parts 1
IC6      MCP6541T-I_OT             MCP6541T-I_OT             SOT95P270X145-5N     SamacSys_Parts 1
J1       INSERT_MM5_06691.5MM      INSERT_MM5_06691.5MM      INSERT_1MM5_9372     FRA_eagle_lib  1
J2       TGS3                      INSERT_MM5_0669           INSERT_MM5_0669      FRA_eagle_lib  1
J3       TGS2                      INSERT_MM5_0669           INSERT_MM5_0669      FRA_eagle_lib  1
J4       TGS1                      INSERT_MM5_0669           INSERT_MM5_0669      FRA_eagle_lib  1
J5       TGS4                      INSERT_MM5_0669           INSERT_MM5_0669      FRA_eagle_lib  1
J6       INSERT_MM5_06691.5MM      INSERT_MM5_06691.5MM      INSERT_1MM5_9372     FRA_eagle_lib  1
J7       INSERT_MM5_06691.5MM      INSERT_MM5_06691.5MM      INSERT_1MM5_9372     FRA_eagle_lib  1
J8       INSERT_MM5_06691.5MM      INSERT_MM5_06691.5MM      INSERT_1MM5_9372     FRA_eagle_lib  1
J9       INSERT_MM5_06691.5MM      INSERT_MM5_06691.5MM      INSERT_1MM5_9372     FRA_eagle_lib  1
J10      2wire                     PINHD-1X2                 1X02                 pinhead        1
LED1                               LEDCHIP-LED0603           CHIP-LED0603         adafruit       1
PS1      AP2202K-ADJTRG1           AP2202K-ADJTRG1           SOT95P280X145-5N     SamacSys_Parts 1
Q1       PMBFJ177,215              PMBFJ177,215              SOT95P230X110-3N     SamacSys_Parts 1
Q3       Si2300DS                  MOSFET-NREFLOW            SOT23                adafruit       1
R1       100k                      R-EU_R0603                R0603                resistor       1
R2       12k                       R-EU_R0603                R0603                resistor       1
R3       5k                        R-EU_R0603                R0603                resistor       1
R4       5.1k                      R-EU_R0603                R0603                resistor       1
R5       10k                       R-EU_R0603                R0603                resistor       1
R6       10k                       R-EU_R0603                R0603                resistor       1
R7       10k                       R-EU_R0603                R0603                resistor       1
R8       10k                       R-EU_R0603                R0603                resistor       1
R9       10                        R-EU_R0603                R0603                resistor       1
R10      10                        R-EU_R0603                R0603                resistor       1
R11      10                        R-EU_R0603                R0603                resistor       1
R12      10                        R-EU_R0603                R0603                resistor       1
R13      0                         R-EU_R0603                R0603                resistor       1
R14      0                         R-EU_R0603                R0603                resistor       1
R15      0                         R-EU_R0603                R0603                resistor       1
R16      0                         R-EU_R0603                R0603                resistor       1
R17      0                         R-EU_R0603                R0603                resistor       1
R18      0                         R-EU_R0603                R0603                resistor       1
R19      10k                       R-EU_R0603                R0603                resistor       1
R20      10k                       R-EU_R0603                R0603                resistor       1
R21      10k                       R-EU_R0603                R0603                resistor       1
R22      0                         R-EU_R0603                R0603                resistor       1
R23      0                         R-EU_R0603                R0603                resistor       1
R24      100                       R-EU_R0603                R0603                resistor       1
R25      100k                      R-EU_R0603                R0603                resistor       1
R26      5.1k                      R-EU_R0603                R0603                resistor       1
R27      100k                      R-EU_R0603                R0603                resistor       1
S$1      FIGARO_2611WITH_INSERTS   FIGARO_2611WITH_INSERTS   TH4_TGS2611_INSERTS  FRA_eagle_lib  1
S$3      CITIPEL_4P50INSERTS       CITIPEL_4P50INSERTS       TH3_4P50_INSERTS     FRA_eagle_lib  1
U$1      CONN_03X2_WE_61200621621  CONN_03X2_WE_61200621621  WE_61200621621       FRA_eagle_lib  1
U$2      TGS5042                   TGS5042                   TGS5042              FRA_eagle_lib  1
X1       3-ELECTRODE-GAS-SENSORINS 3-ELECTRODE-GAS-SENSORINS 3-ELECTRODE_INSETRS  gas-sensor     1

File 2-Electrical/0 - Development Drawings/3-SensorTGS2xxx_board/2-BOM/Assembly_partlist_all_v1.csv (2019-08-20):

Partlist
Exported from FRA_Sensor_TGS2xxx.brd at 16-Aug-19 13:45
EAGLE Version 7.6.0 Copyright (c) 1988-2016 CadSoft
Assembly variant:
Part     Value          Package          Library        Position (mm)         Orientation
C1       100n           C0603K           resistor       (15.355 28.544)       R180
C2       100n           C0603K           resistor       (8.385 11.022)        R0
C3       100n           C0603K           resistor       (2.115 23.265)        R0
C9       1n             C0603K           resistor       (12.417 11.033)       R180
C10      1n             C0603K           resistor       (3.983 12.292)        R270
C13      100n           C0603K           resistor       (15.75 12.555)        R0
FB1                     0603             microbuilder   (11.22 17.452)        R180
FB9                     0603             microbuilder   (10.409 13.299)       R0
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

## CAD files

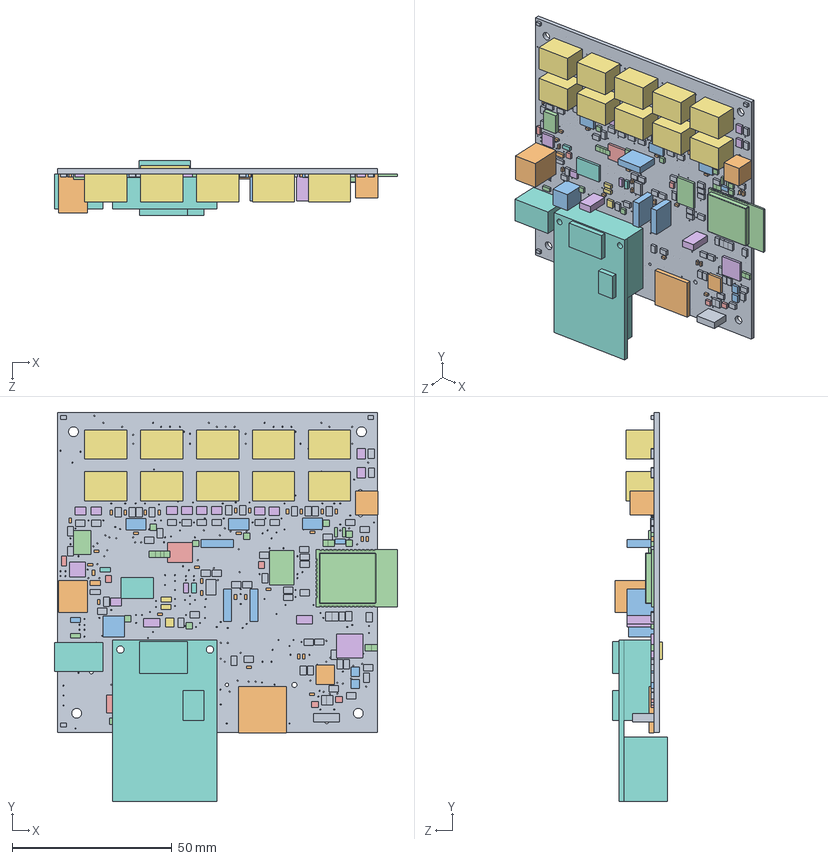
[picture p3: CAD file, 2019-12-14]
4-Mechanical/PCB_model/fra_sensor_v1.SLDASM
107.3 x 121.6 x 17.1 mm
fra_sensor_v1
C0603K_C0603K x 45
153CLV0605_153CLV0605
C0402_C0402 x 2
SOT323R_PESD1CANSC70 x 4
1X02_1X02 x 2
0603_FB1_0603
0603_FB2_0603
0603_FB3_0603
0603_FB4_0603
0603_FB5_0603
0603_FB6_0603
0603_FB7_0603
0603_FB8_0603
0603_FB9_0603
0603_FB10_0603
FIDUCIAL_1MM_FIDUCIAL__ x 3
MLP28_CP2101
SOP50P490X11010N_1100000_ADS1115IDGSR_1100000 x 3
SOIC127P600X1758N_1750000_P82B715DR_1750000
TSSOP24_PCA9555PW
STSOT89_LDK320ADU50R
2X6_ETH_CONN
PJ059A_11000000_PJ059A_11000000
USBBMICROSMD_VERT_WM9734TRND
1X04_1X04 x 3
2X05_1_27MM_SMT_DNI
SRP5030CA_SRP5030CA1R5M x 2
SOT23WIDE_FDN306P x 11
SOT23_SI2300DS
TO252_DNI
R0603_R0603 x 74
B3F31XX_S1_B3F31XX
SOT23_BC847 x 2
TP10R_TPTP10R x 20
SOT236_TPS563249DDCR x 2
2X03_1_27MM_SMT_DNI
WE_61200621621_CONN_03X2_WE_61200621621 x 10
ETH_MODULE_OUTLINE_SMALL_ETH_MODULE_OUTLINE
SOT5051_PCA9509DP
W237102_W237102
CRYSTALSMD3_2X1_5MM_DNI
esp32wroom

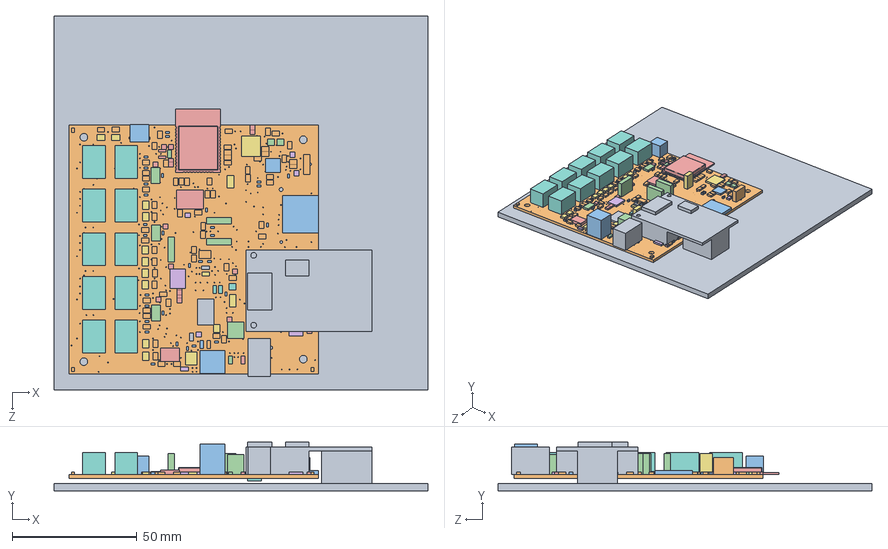
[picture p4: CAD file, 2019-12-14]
4-Mechanical/BOX_top_all.SLDASM
150.0 x 19.6 x 150.0 mm
BOX_bottom
fra_sensor_v1
C0603K_C0603K x 45
153CLV0605_153CLV0605
C0402_C0402 x 2
SOT323R_PESD1CANSC70 x 4
1X02_1X02 x 2
0603_FB1_0603
0603_FB2_0603
0603_FB3_0603
0603_FB4_0603
0603_FB5_0603
0603_FB6_0603
0603_FB7_0603
0603_FB8_0603
0603_FB9_0603
0603_FB10_0603
FIDUCIAL_1MM_FIDUCIAL__ x 3
MLP28_CP2101
SOP50P490X11010N_1100000_ADS1115IDGSR_1100000 x 3
SOIC127P600X1758N_1750000_P82B715DR_1750000
TSSOP24_PCA9555PW
STSOT89_LDK320ADU50R
2X6_ETH_CONN
PJ059A_11000000_PJ059A_11000000
USBBMICROSMD_VERT_WM9734TRND
1X04_1X04 x 3
2X05_1_27MM_SMT_DNI
SRP5030CA_SRP5030CA1R5M x 2
SOT23WIDE_FDN306P x 11
SOT23_SI2300DS
TO252_DNI
R0603_R0603 x 74
B3F31XX_S1_B3F31XX
SOT23_BC847 x 2
TP10R_TPTP10R x 20
SOT236_TPS563249DDCR x 2
2X03_1_27MM_SMT_DNI
WE_61200621621_CONN_03X2_WE_61200621621 x 10
ETH_MODULE_OUTLINE_SMALL_ETH_MODULE_OUTLINE
SOT5051_PCA9509DP
W237102_W237102
CRYSTALSMD3_2X1_5MM_DNI
esp32wroom

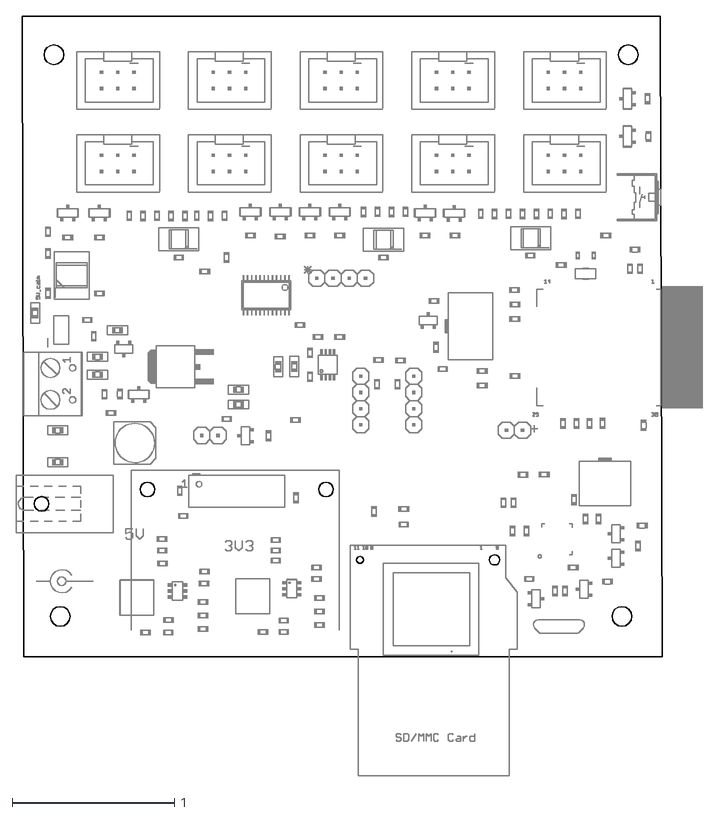
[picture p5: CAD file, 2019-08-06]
2-Electrical/0 - Development Drawings/1 - Main Board/4 - Assembly Drawings/FRA_Sensor_v1.dxf
4.24 x 4.68

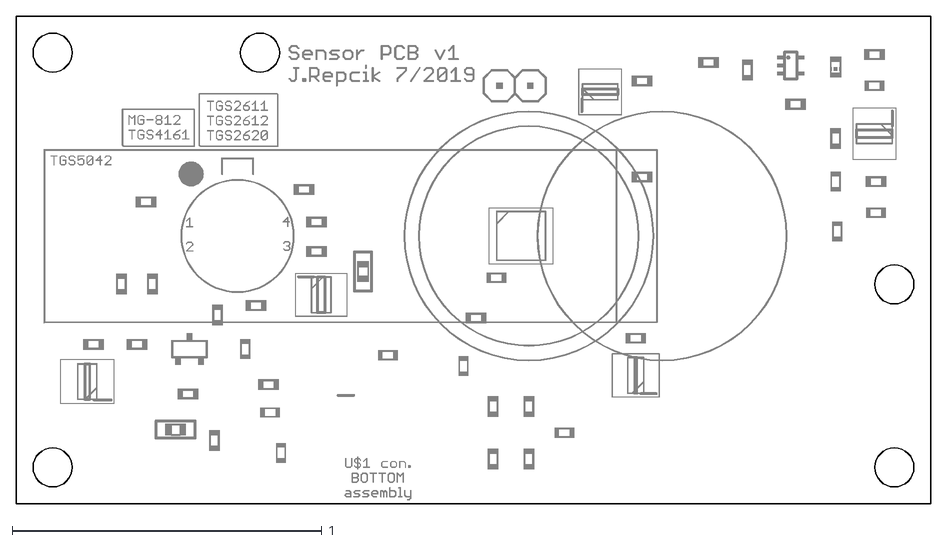
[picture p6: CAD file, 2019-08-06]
2-Electrical/0 - Development Drawings/2-SensorBoard/4-Drawings/FRA_daughter_v1.dxf
2.95 x 1.57

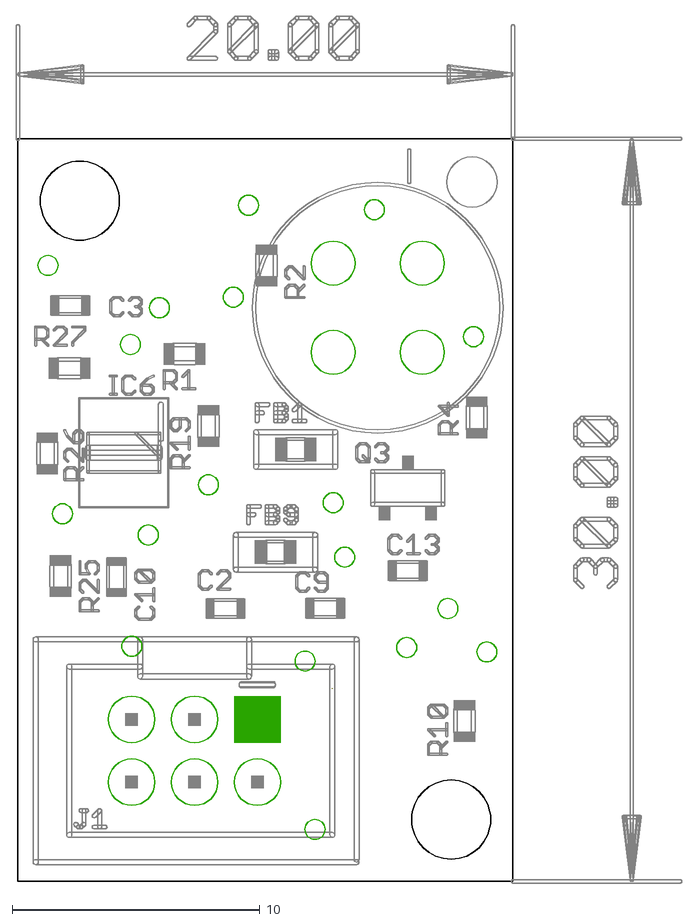
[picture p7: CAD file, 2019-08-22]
2-Electrical/0 - Development Drawings/3-SensorTGS2xxx_board/4-Drawings/FRA_Sensor_TGS2xxx.dxf
26.9 x 35.0

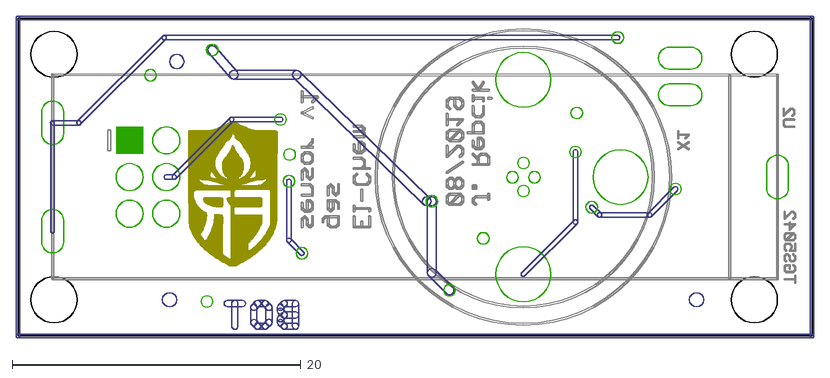
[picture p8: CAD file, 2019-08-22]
2-Electrical/0 - Development Drawings/4-SensorElChem_board/4-Drawings/Sensor_PCB_Electrochemical.dxf
55.2 x 22.3

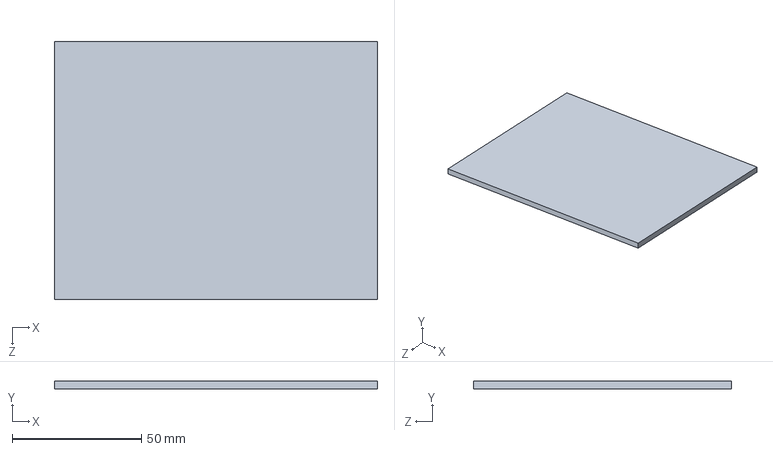
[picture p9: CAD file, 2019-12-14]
4-Mechanical/BOX_bottom.SLDPRT
125.0 x 3.00 x 100.0 mm

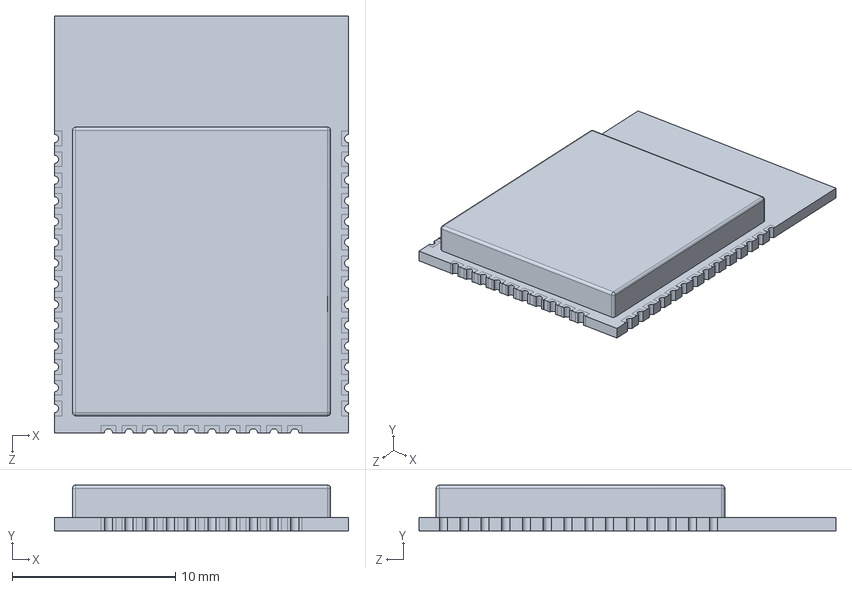
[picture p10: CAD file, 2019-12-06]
4-Mechanical/PCB_model/submodels/esp32wroom.SLDPRT
18.0 x 2.81 x 25.5 mm

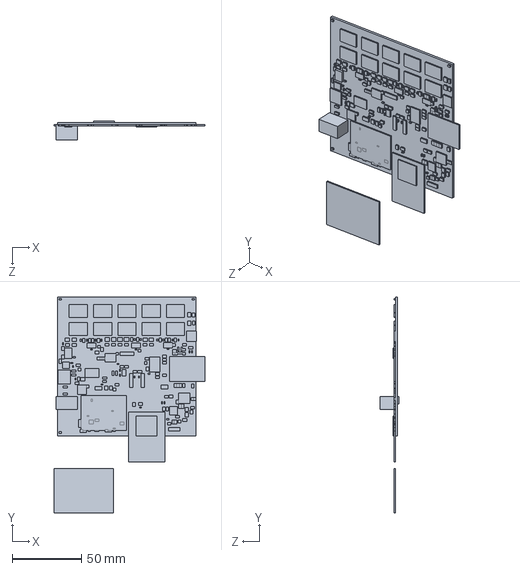
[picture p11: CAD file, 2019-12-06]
4-Mechanical/FRA_Sensor_v1_SW.SLDPRT
108.8 x 155.6 x 13.6 mm

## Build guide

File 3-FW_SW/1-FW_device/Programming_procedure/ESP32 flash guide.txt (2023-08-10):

1. Get location of binary files: - skip these step if you alteady have binary files
Run terminal in platformio (icon next to serial monitor on lower bar)
Enter command>
pio run -v -t upload

See in output:
"d:\cadence\spb_data\.platformio\penv\scripts\python.exe" "D:\Cadence\SPB_Data\.platformio\packages\tool-esptoolpy\esptool.py" 
--chip esp32 
--port "COM7" 
--baud 921600 
--before default_reset 
--after hard_reset
write_flash -z 
--flash_mode dio 
--flash_freq 40m 
--flash_size detect 
0x1000 D:\Cadence\SPB_Data\.platformio\packages\framework-arduinoespressif32\tools\sdk\bin\bootloader_dio_40m.bin 
0x8000 D:\PROJECTS\01_GIT_REPOS\FRA_Sensor_platform\3-FW_SW\1-FW_device\FRA_SP_ESP32v2\.pio\build\FRAunit_COM7\partitions.bin 
0xe000 D:\Cadence\SPB_Data\.platformio\packages\framework-arduinoespressif32\tools\partitions\boot_app0.bin 
0x10000 .pio\build\FRAunit_COM7\firmware.bin

2. Use ESP32 download tool to flash.
Select ESP32 DownloadTool
Configure as follows:

0x1000 bootloader_dio_40m.bin 
0x8000 partitions.bin 
0xe000 boot_app0.bin 
0x10000 firmware.bin

3. if there are issues, try different UART converter (ESP-prog instead built in on board)
and update esptool folder from
https://github.com/espressif/esptool

4. In case of issue:
"A fatal error occurred: Failed to connect to ESP32: Timed out waiting for packet header"
Several solutions:
* short GPIO0 to GND in connecting (sync) phase. Short is easiest on U$2 connector, pins 4+6 (ones closest to R7)
* Or change C16 from 100n to 4.7uF (or 10uF).
* or use some different version of esptool? (not tested)

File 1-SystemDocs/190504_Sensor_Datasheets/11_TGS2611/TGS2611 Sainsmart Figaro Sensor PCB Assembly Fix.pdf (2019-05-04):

1
Written by David Anderson 30th December 2014

Sainsmart Figaro Sensor PCB Assembly Fix and Connection to Arduino UNO

The Figaro Sensor (4-Pin) (e.g. TGS 2611) PCB Assembly from Sainsmart has been shipped from the factory, with the Sensor incorrectly soldered to the PCB. A quick internet search shows pictures of ALL 4-pin Figaro sensors to be soldered this way (i.e. INCORRECT). If the PCB is connected to an Arduino, as received form the factory, it will not work correctly. This document describes a fix for this problem, and shows how to connect it to an Arduino (Sainsmart) UNO for testing.

Problem Description

The Figaro sensor, (TGS2611), PCB assembly was received from Sainsmart and connected to a UNO (see later in the document for full instructions and code on how to connect this up), with the Analog Output from the Sensor monitored. A constant High Value of ~4.74V was measured on the Output and no change in the Output was detected when the sensor was exposed to Organic Vapours. Upon investigation, it was discovered the Figaro Sensor is incorrectly soldered to the PCB. The PCB the sensor comes soldered onto is a generic PCB which is primarily used for the 6-Pin MQ (and Figaro) type sensors. For these 6-pin sensors, the heater pins are in the central location of the PCB. The 4-Pin Sensor therefore needs to be moved so the heater pins are in the central position. This also explains the constant value of 4.74V on the output, as this is the constant voltage through the Heater.

Fix

The Heater Pins (1 and 4) of the 4-Pin sensor should be moved to the central positions of the PCB. These are the Pins on the NOTCH side of the Sensor. The Sensor Electrode Pins should be in the outer positions of the PCB. See the diagram below for Pin numbers of the Figaro 4-Pin sensor – full datasheets can be found here: www.figarosensor.com/gaslist.html.

This involves de-soldering the sensor, moving it to the correct position and then re-soldering. If you are new to soldering take care not to heat the sensor legs too much as this can damage the sensor element.

See below for pictures of how the sensor should be soldered.

2

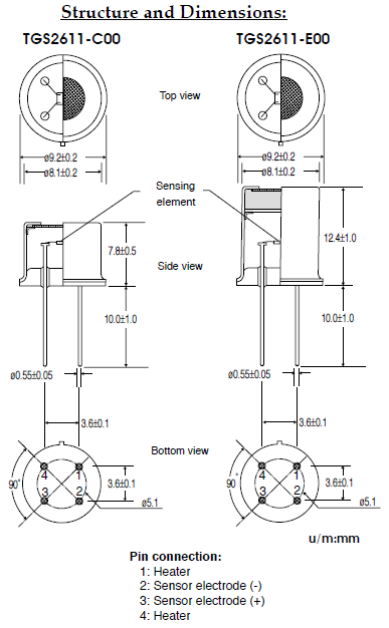
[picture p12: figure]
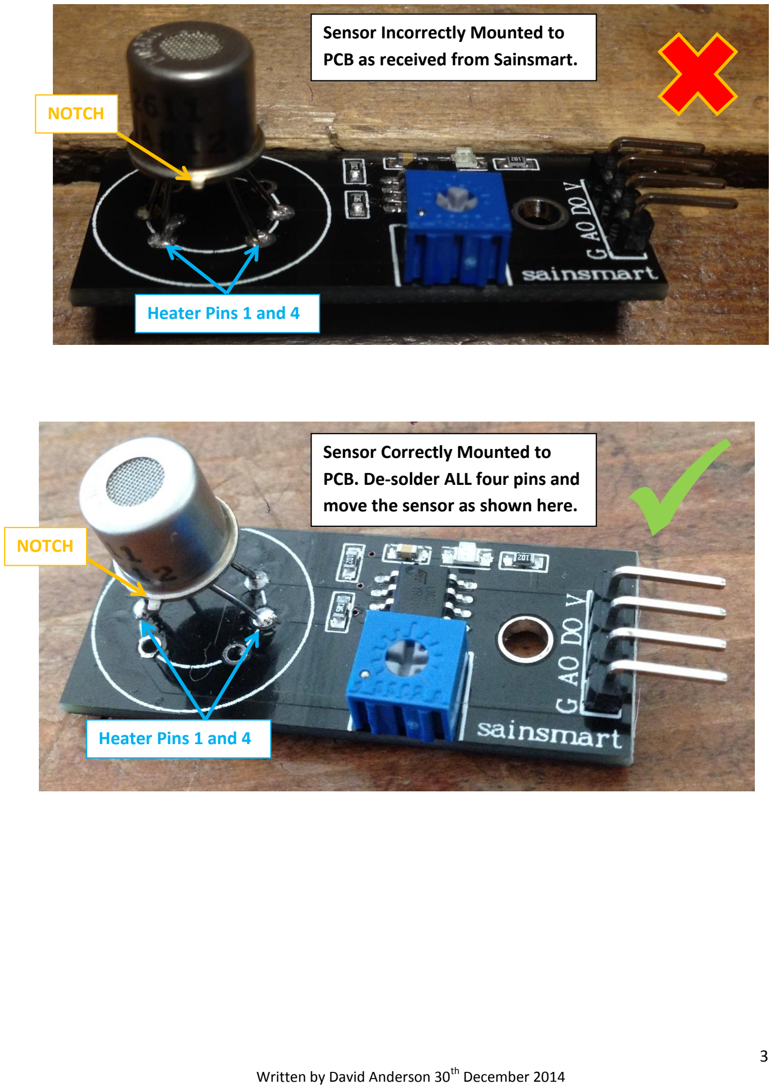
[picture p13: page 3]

3

Sensor Incorrectly Mounted to PCB as received from Sainsmart.

Heater Pins 1 and 4

NOTCH

✓
Sensor Correctly Mounted to PCB. De-solder ALL four pins and move the sensor as shown here.

Heater Pins 1 and 4

NOTCH

4

Connection to the Arduino (Sainsmart) Uno and Test

To measure the Analog Output of the Sensor, connect the Wiring as follows:

UNO | Sensor PCB
5V | V
GND | G
A0 | AO

(Note: ‘DO’ on the Sensor PCB is the Digital Out – this can be adjusted to switch from Low to High, with the Trim Pot, when the Sensor is exposed to Solvent Vapour – this is not covered in this topic).

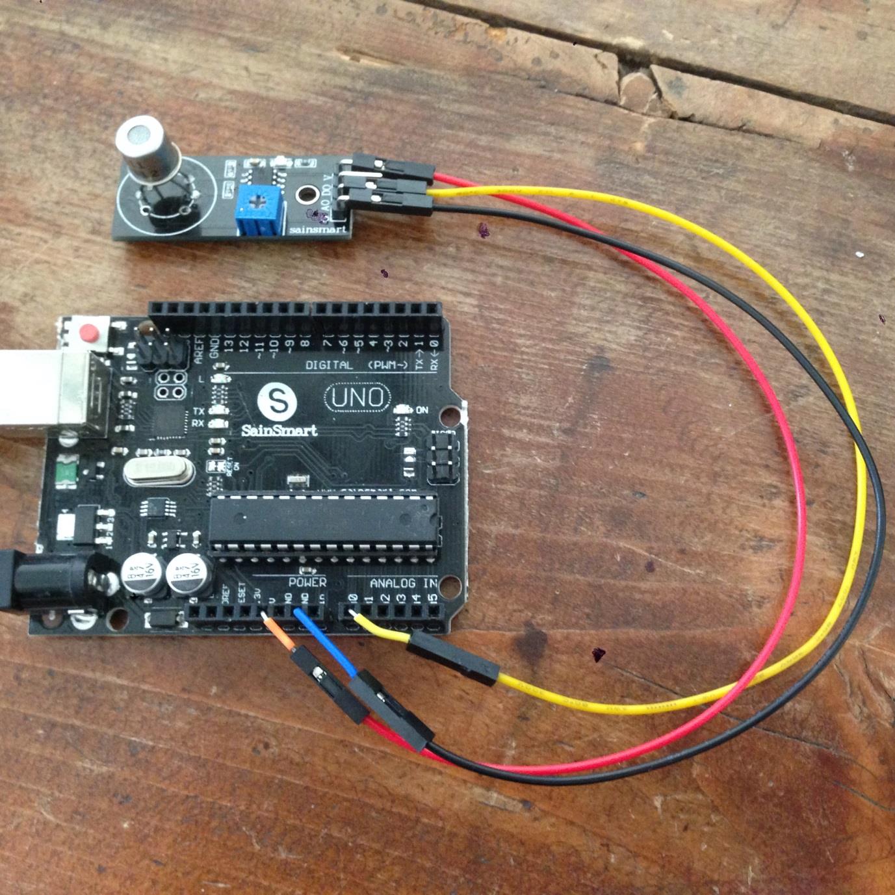
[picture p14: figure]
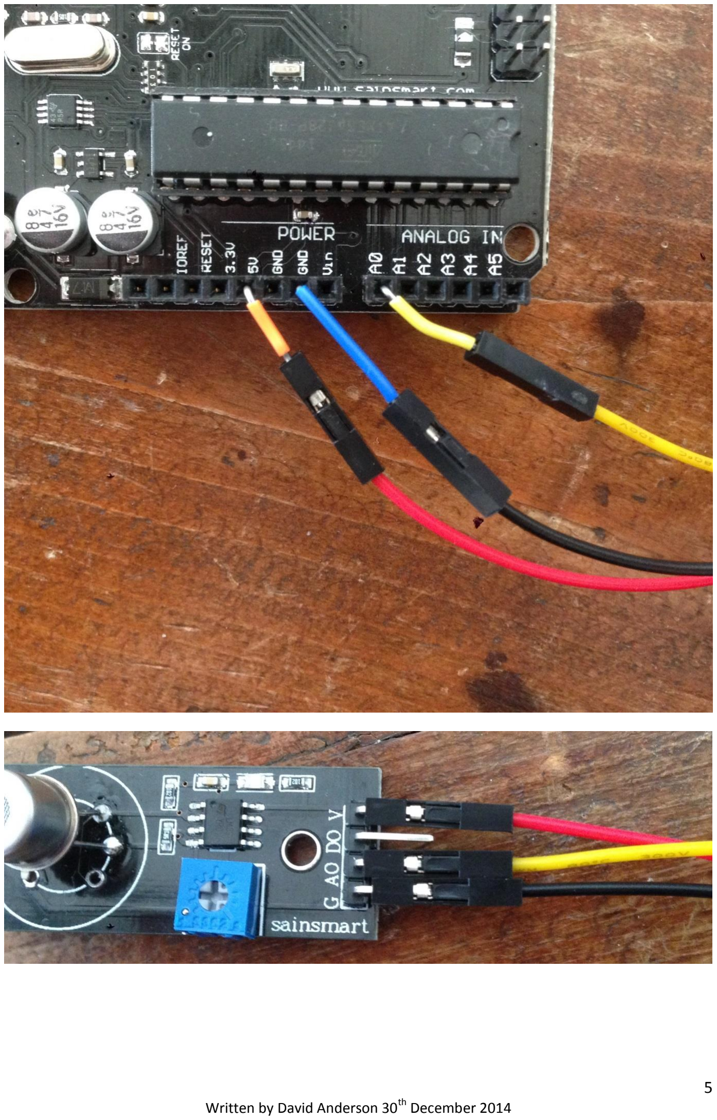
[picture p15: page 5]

5

6

Upload the following code to the UNO:

/*

ReadAnalogVoltage

Reads an analog input on pin 0, converts it to voltage, and prints the result to the serial monitor.

Attach the center pin of a potentiometer to pin A0, and the outside pins to +5V and ground.

This example code is in the public domain.

*/

// the setup routine runs once when you press reset:

void setup() {

// initialize serial communication at 9600 bits per second:

Serial.begin(9600);

}

// the loop routine runs over and over again forever:

void loop() {

// read the input on analog pin 0:

int sensorValue = analogRead(A0);

// Convert the analog reading (which goes from 0 - 1023) to a voltage (0 - 5V):

float voltage = sensorValue * (5.0 / 1023.0);

// print out the value you read:

Serial.println(voltage);

}

7

Now open ‘Serial Monitor’ in the Arduino Sketch software – you should see the Output value at around ~0.2V. Blow on the Sensor – you should see the value increase and then drop back down. Test with a solvent vapour held near the sensor – the value should increase greatly, >1V. When the solvent source is removed, the output should drop back to its baseline value. If this is the case, congratulations you now have a working sensor.

Thanks for reading – I hope this helps a few people out.

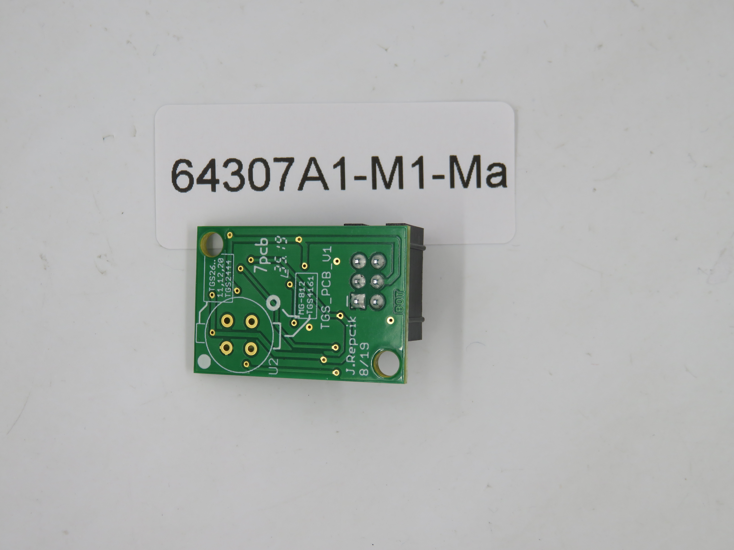
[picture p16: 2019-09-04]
2-Electrical/0 - Development Drawings/3-SensorTGS2xxx_board/8-Manufacturing/M1_variantA-TGS26xx/64307A1-M1/64307A1-M1-B.JPG

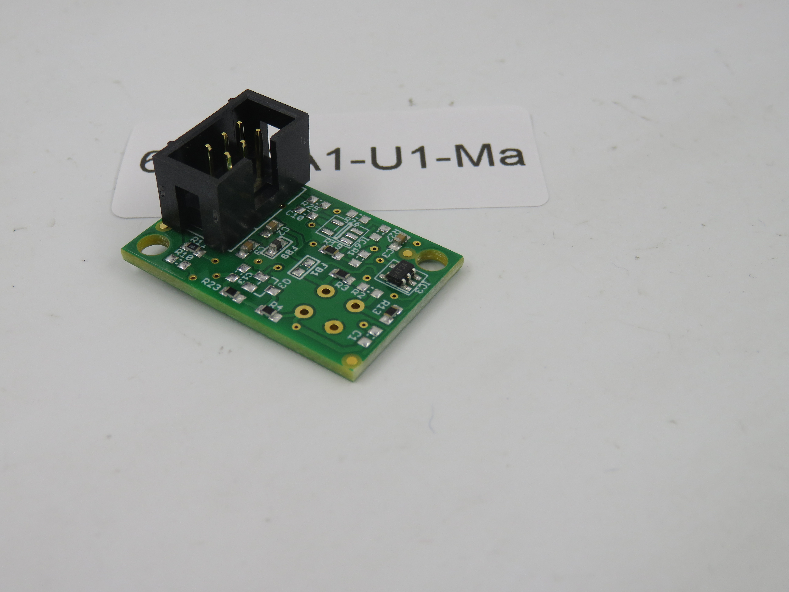
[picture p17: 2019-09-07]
2-Electrical/0 - Development Drawings/3-SensorTGS2xxx_board/8-Manufacturing/U1_variantC_CO2/64307A1-U1/IMG_9068.JPG

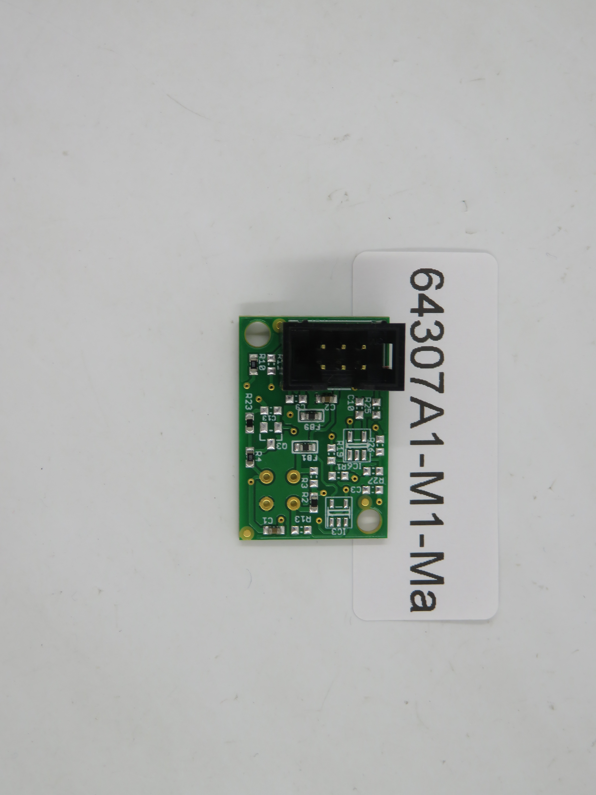
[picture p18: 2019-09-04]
2-Electrical/0 - Development Drawings/3-SensorTGS2xxx_board/8-Manufacturing/M1_variantA-TGS26xx/64307A1-M1/64307A1-M1-T.JPG

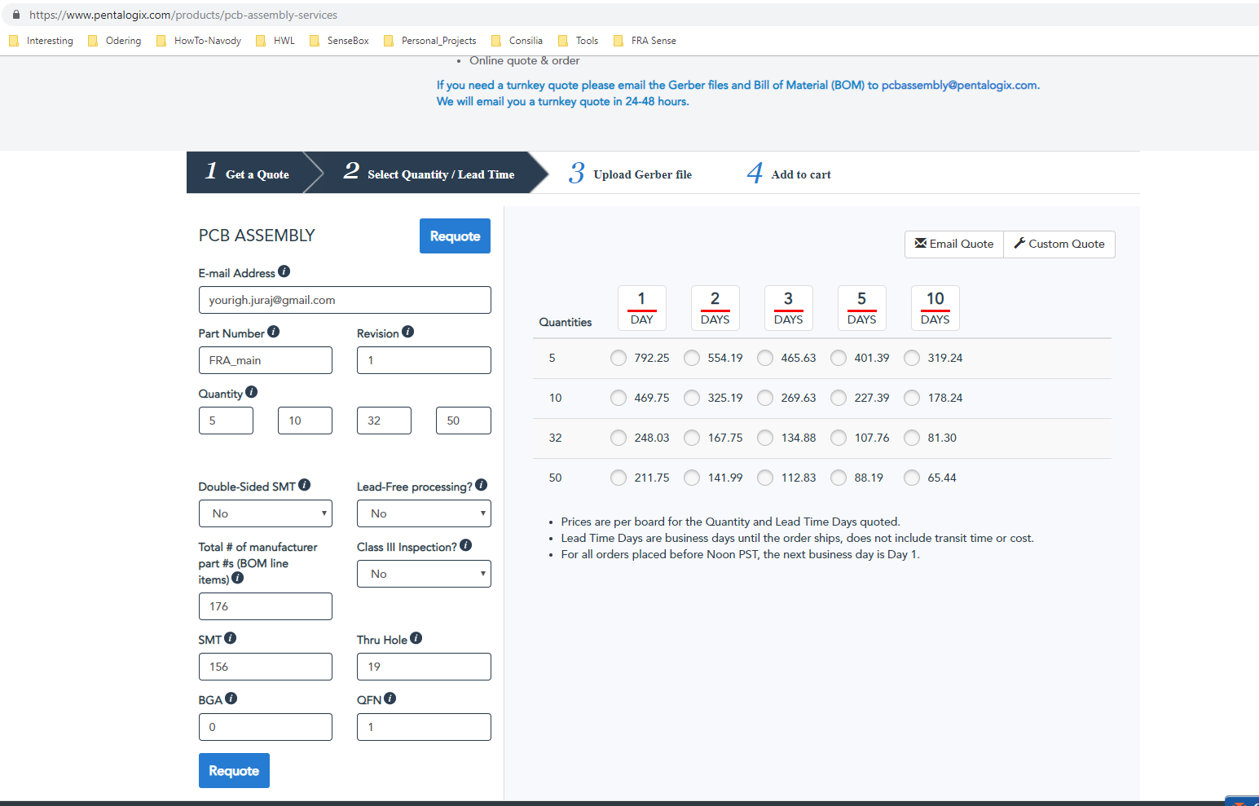
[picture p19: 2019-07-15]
1-SystemDocs/Orders/Assembly_Quote.PNG

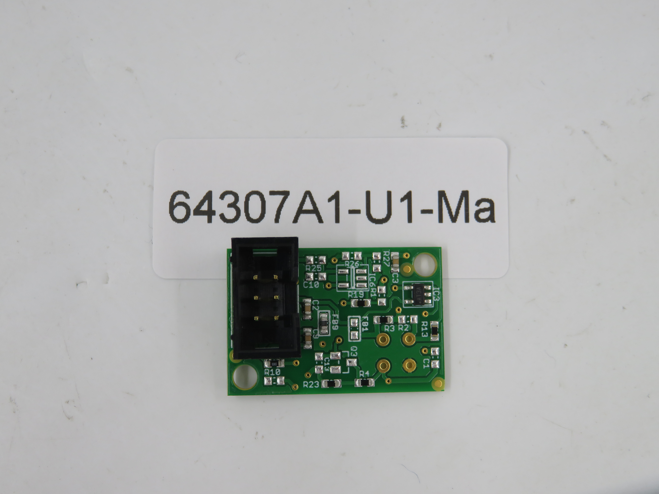
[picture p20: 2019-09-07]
2-Electrical/0 - Development Drawings/3-SensorTGS2xxx_board/8-Manufacturing/U1_variantC_CO2/64307A1-U1/64307A1-U1-T.JPG

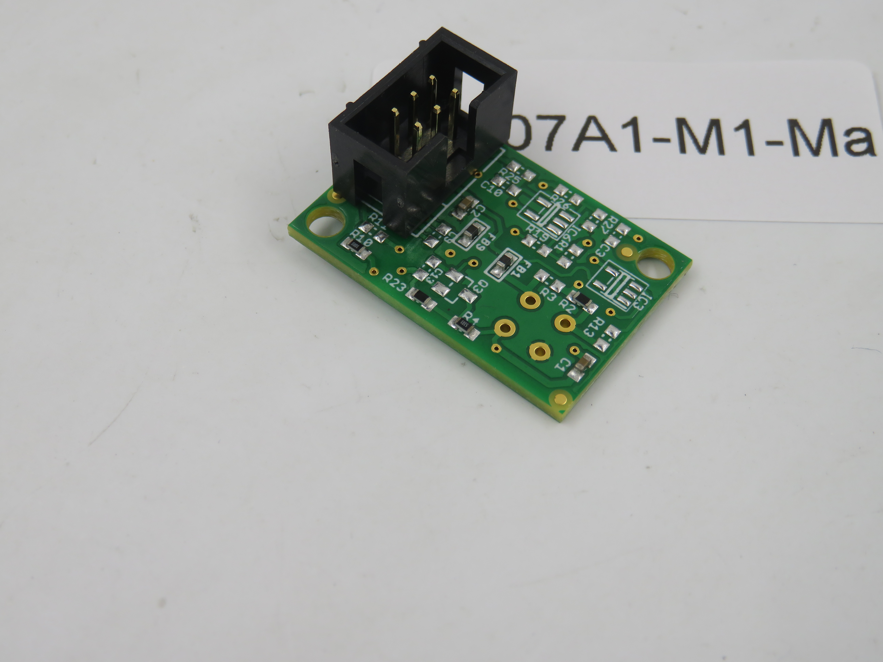
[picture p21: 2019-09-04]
2-Electrical/0 - Development Drawings/3-SensorTGS2xxx_board/8-Manufacturing/M1_variantA-TGS26xx/64307A1-M1/IMG_9054.JPG

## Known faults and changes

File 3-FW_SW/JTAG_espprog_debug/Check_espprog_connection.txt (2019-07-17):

d:
cd D:\Cadence\SPB_Data\.platformio\packages\tool-openocd-esp32\bin
openocd -f interface/ftdi/esp32_devkitj_v1.cfg -f board/esp-wroom-32.cfg

OK vypis:
? openocd -f interface/ftdi/esp32_devkitj_v1.cfg -f board/esp-wroom-32.cfg
Open On-Chip Debugger  v0.10.0-esp32-20190708 (2019-07-08-11:04)
Licensed under GNU GPL v2
For bug reports, read
        http://openocd.org/doc/doxygen/bugs.html
none separate
adapter speed: 10000 kHz
Info : Configured 2 cores
esp32 interrupt mask on
Info : Listening on port 6666 for tcl connections
Info : Listening on port 4444 for telnet connections
Error: libusb_open() failed with LIBUSB_ERROR_NOT_SUPPORTED
Info : ftdi: if you experience problems at higher adapter clocks, try the command "ftdi_tdo_sample_edge falling"
Info : clock speed 10000 kHz
Info : JTAG tap: esp32.cpu0 tap/device found: 0x120034e5 (mfg: 0x272 (Tensilica), part: 0x2003, ver: 0x1)
Info : JTAG tap: esp32.cpu1 tap/device found: 0x120034e5 (mfg: 0x272 (Tensilica), part: 0x2003, ver: 0x1)
Info : Detected debug stubs @ 3ffc1034 on core0 of target 'esp32'
Info : Listening on port 3333 for gdb connections
shutdown command invoked
Info : Restore debug stubs @ 3ffc1034 on core0 of target 'esp32'
Warn : Flash driver of esp32.flash does not support free_driver_priv()
Warn : Flash driver of irom does not support free_driver_priv()

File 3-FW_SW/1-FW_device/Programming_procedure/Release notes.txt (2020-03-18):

V1.2 - electrochemical sensor port A3.1 configuration fixed
V1.3 - updated configuration sets
V1.4 - added configuration set 6
V1.5 - changed A1.3 REFCN register, fixed bug on conf set 5 and 6 (0x04 instead of 0x40)
V1.6 changelog
SDFat lib dependency fixed in project - now included in the project, EEPROM init failed and was skipped, test ok
V1.7 changelog
Button can now start and stop measurement (before only start was possible)
Static IP will be used if button pressed at least 1s on DHCP wait time and after wait time.
V1.8 changelog
*confuguration set 7 added (4xO2 sensor on all A1 ports)

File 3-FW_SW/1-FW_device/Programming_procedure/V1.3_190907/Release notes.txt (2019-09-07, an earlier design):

V1.2 - electrochemical sensor port A3.1 configuration fixed
V1.3 - updated configuration sets

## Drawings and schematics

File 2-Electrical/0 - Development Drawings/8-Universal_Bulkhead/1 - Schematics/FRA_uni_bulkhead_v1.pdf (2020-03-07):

A

A

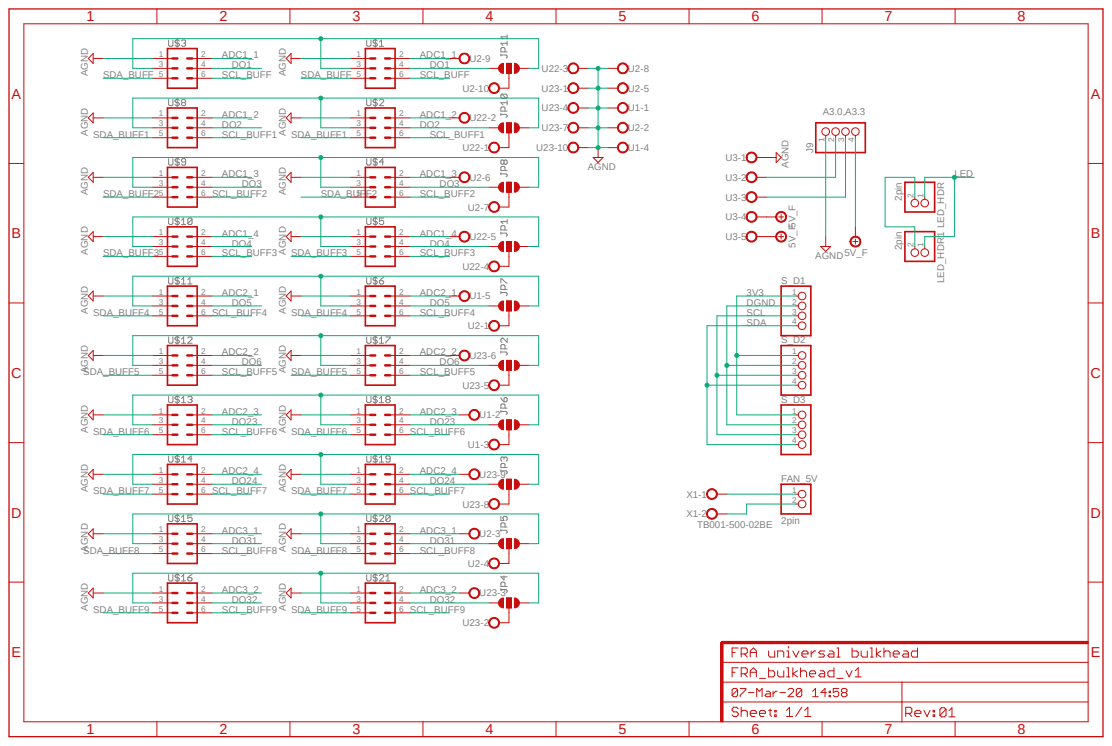
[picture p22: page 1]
A3.0,A3.3 AGND AGND AGND AGND AGND AGND AGND AGND AGND AGND; AGND AGND AGND AGND AGND AGND AGND AGND AGND AGND; AGND5V_F; 2pin; AGND; 2pin AGND 5V_F; 2 FAN_5V; 1 LED_HDR; 1 LED_HDR1; ADC1_1; ADC1_2; ADC1_3; ADC1_4; ADC2_1; ADC2_2; ADC2_3; ADC2_4; ADC3_1; ADC3_2; SDA_BUFF; SDA_BUFF SCL_BUFF; SCL_BUFF; LED; 3V3 DGND; SDA_BUFF1; SDA_BUFF1 SCL_BUFF1; SCL_BUFF1; SDA_BUFF2; SDA_BUFF2 SCL_BUFF2; SCL_BUFF2; SDA_BUFF3; SDA_BUFF3 SCL_BUFF3; SCL_BUFF3; SDA_BUFF4; SDA_BUFF4 SCL_BUFF4; SCL_BUFF4; SDA_BUFF5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

SCL | 3
SDA

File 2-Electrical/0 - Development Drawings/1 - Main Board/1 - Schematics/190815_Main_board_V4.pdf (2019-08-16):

A

A

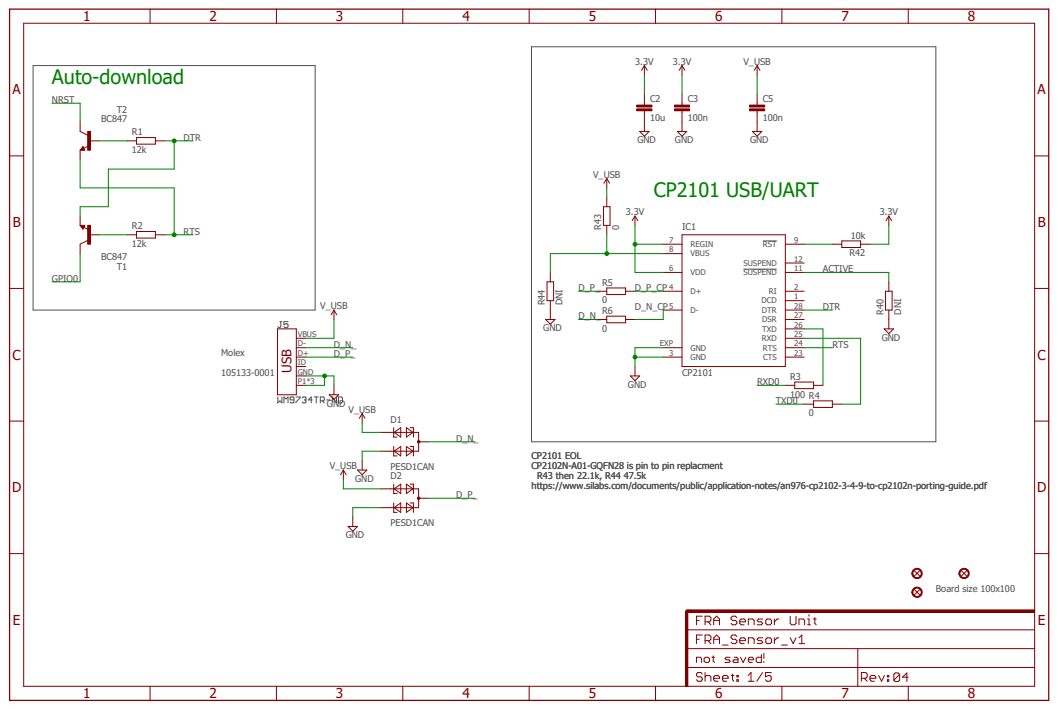
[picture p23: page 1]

CP2101 EOL
CP2102N-A01-GQFN28 is pin to pin replacment
R43 then 22.1k, R44 47.5k
https://www.silabs.com/documents/public/application-notes/an976-cp2102-3-4-9-to-cp2102n-porting-guide.pdf

# POWER

R22R²⁸ | R²⁹ | R³⁰

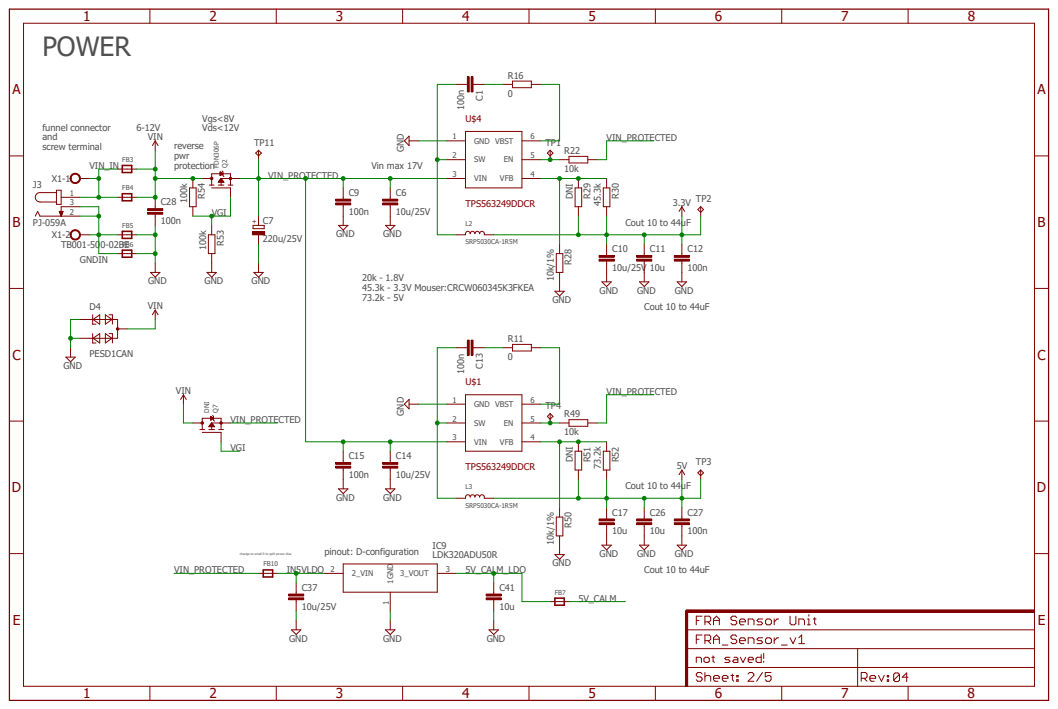
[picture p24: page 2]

A

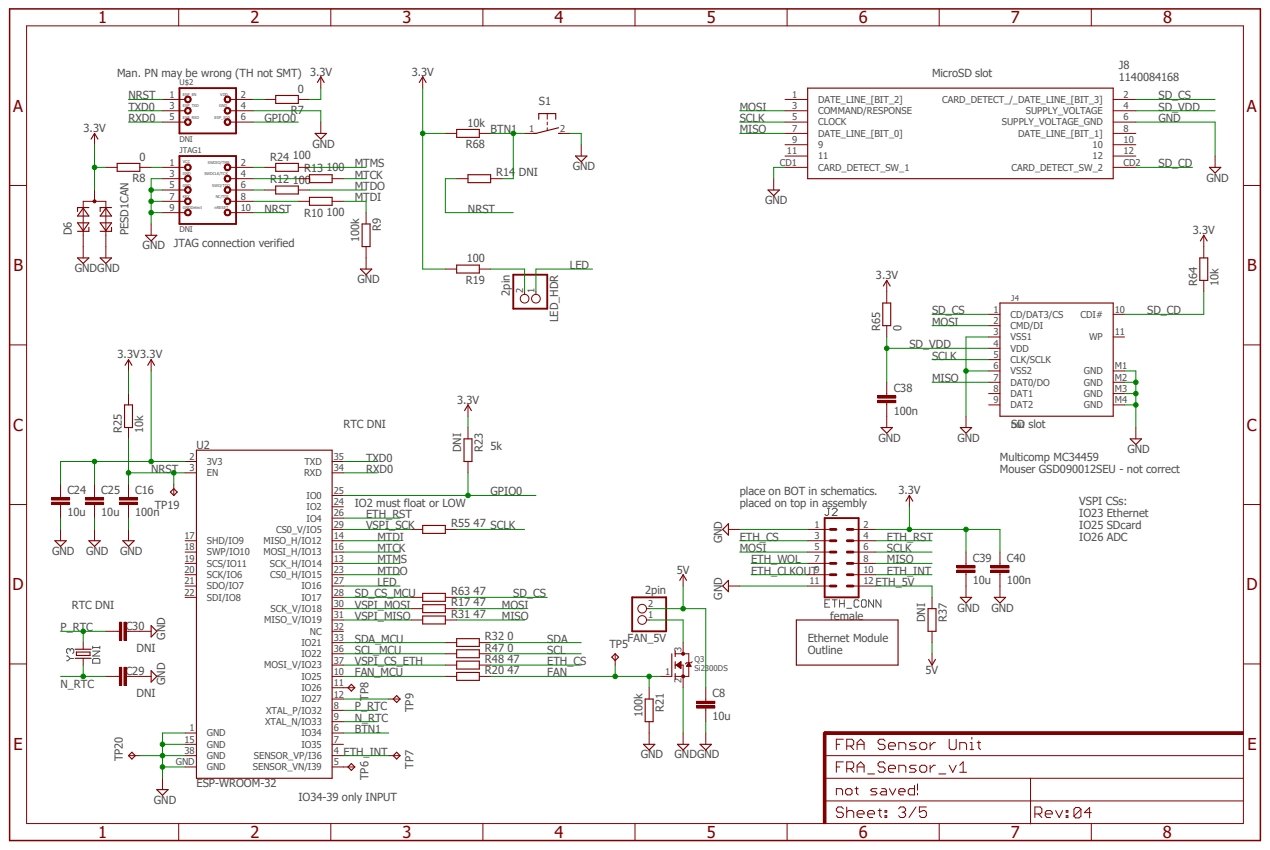
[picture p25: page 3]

3.3V GND
place on BOT in schematics.
placed on top in assembly

A

A

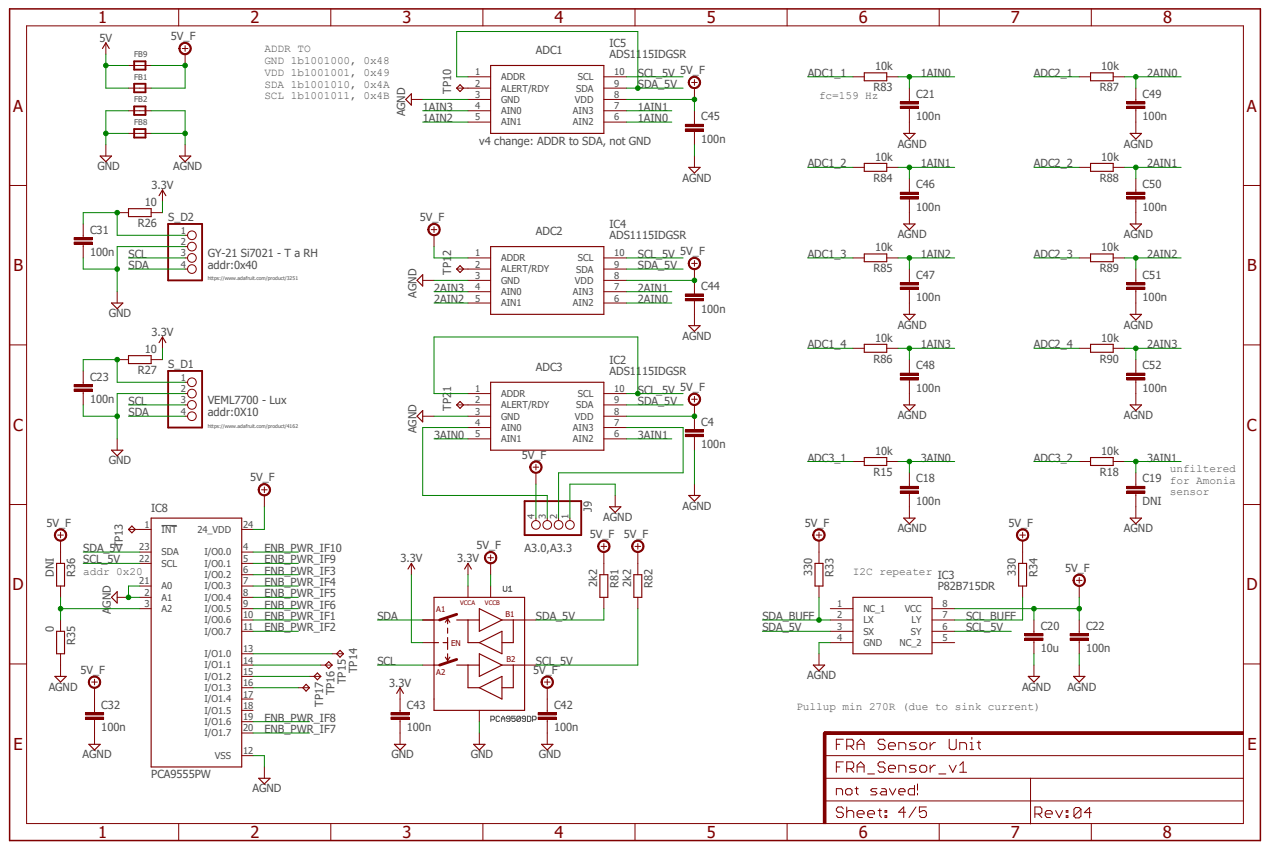
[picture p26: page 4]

https://www.adafruit.com/product/3251

https://www.adafruit.com/product/4162

Pullup min 270R (due to sink current)

# 5V_F ¹³

SCL_BUFF ABCDE | 1 | 2 | 3 | 4 | 5 | 6 | 7 | 8 | ABCDE 1 | 2 | 3 | 4 | 5 | 6 | 7 | 8

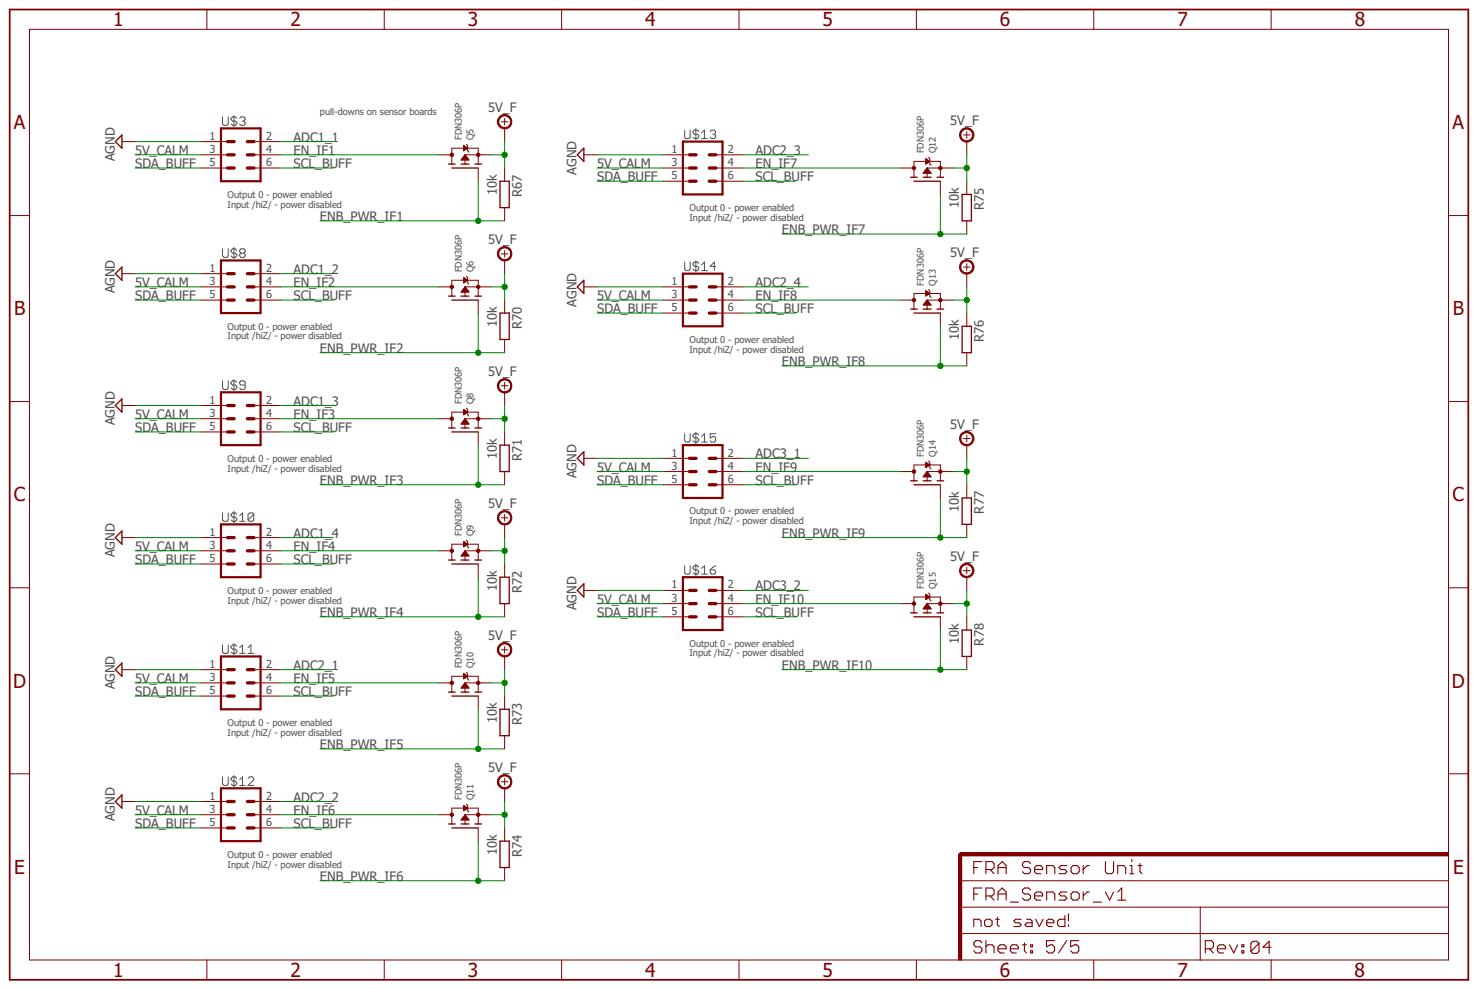
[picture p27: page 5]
pull-downs on sensor boards AGND; FDN³⁰⁶P; 10k AGND; AGND; R⁶⁷ 13; R⁷⁰ 13; R⁷¹ 13; R⁷² 13; Q¹⁰; R⁷³ 13; Q¹¹; R⁷⁴; Q¹²; R⁷⁵ 13; Q¹³; R⁷⁶ 13; Q¹⁴; R⁷⁷ 13; Q¹⁵; R⁷⁸; ADC1_1; 5V_CALM; ENB_PWR_IF1; ADC1_2 EN_IF2; ENB_PWR_IF2; ADC1_3 EN_IF3; ENB_PWR_IF3; ENB_PWR_IF4; ADC1_4; ADC2_1 EN_IF5; ENB_PWR_IF5; ENB_PWR_IF6; ADC2_2; ADC2_3; ADC2_4; ADC3_1; ADC3_2; ENB_PWR_IF10; ENB_PWR_IF9; ENB_PWR_IF8; ENB_PWR_IF7; SDA_BUFF; SCL_BUFF

Output 0 - power enabled
Input /hiZ/ - power disabled

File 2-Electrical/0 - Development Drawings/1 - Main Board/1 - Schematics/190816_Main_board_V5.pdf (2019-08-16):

A

A

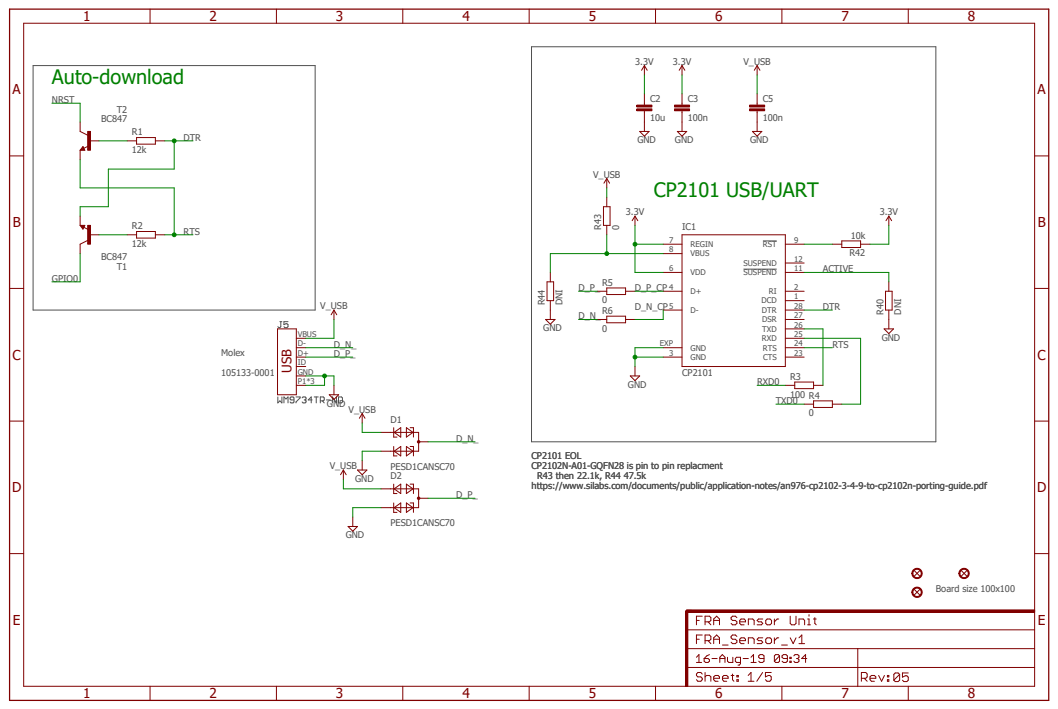
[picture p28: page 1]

CP2101 EOL
CP2102N-A01-GQFN28 is pin to pin replacment
R43 then 22.1k, R44 47.5k
https://www.silabs.com/documents/public/application-notes/an976-cp2102-3-4-9-to-cp2102n-porting-guide.pdf

# POWER

R22R²⁸ | R²⁹ | R³⁰

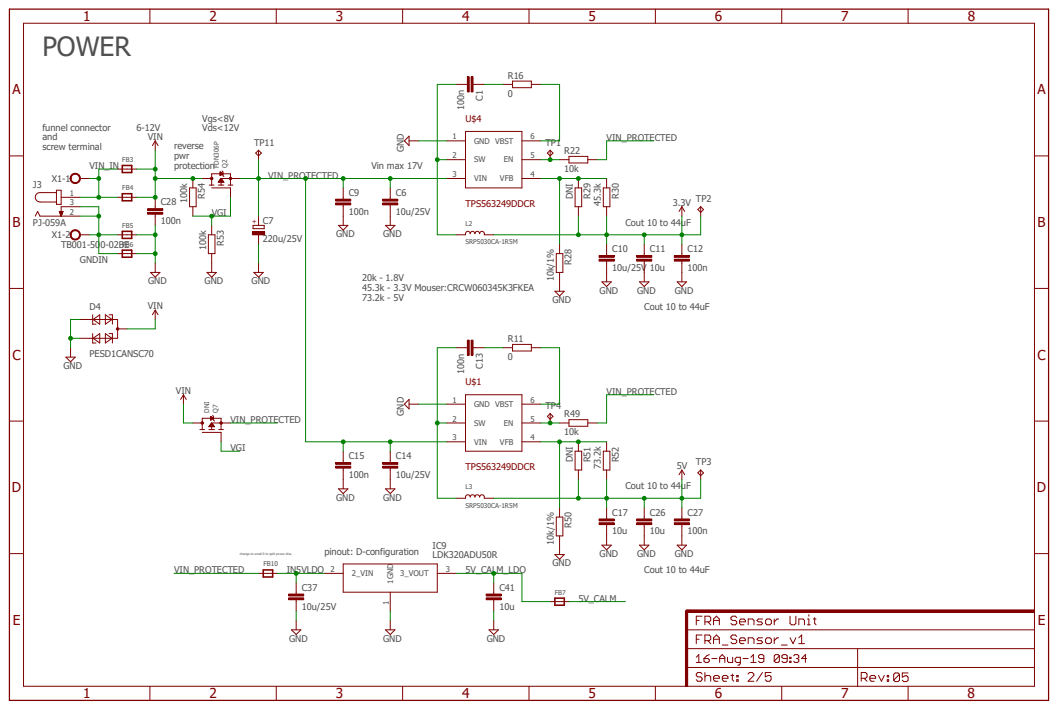
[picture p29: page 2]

A

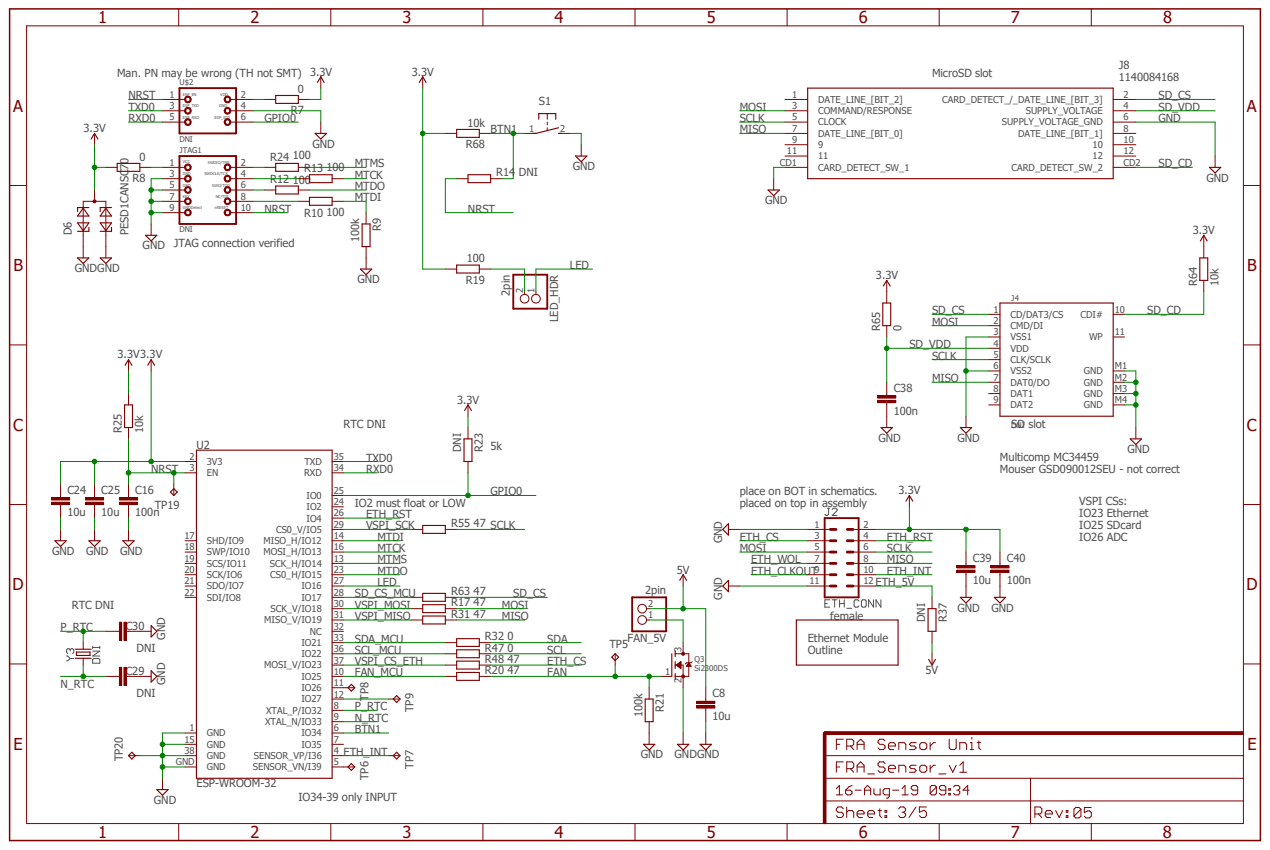
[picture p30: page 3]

3.3V GND
place on BOT in schematics.
placed on top in assembly

A

A

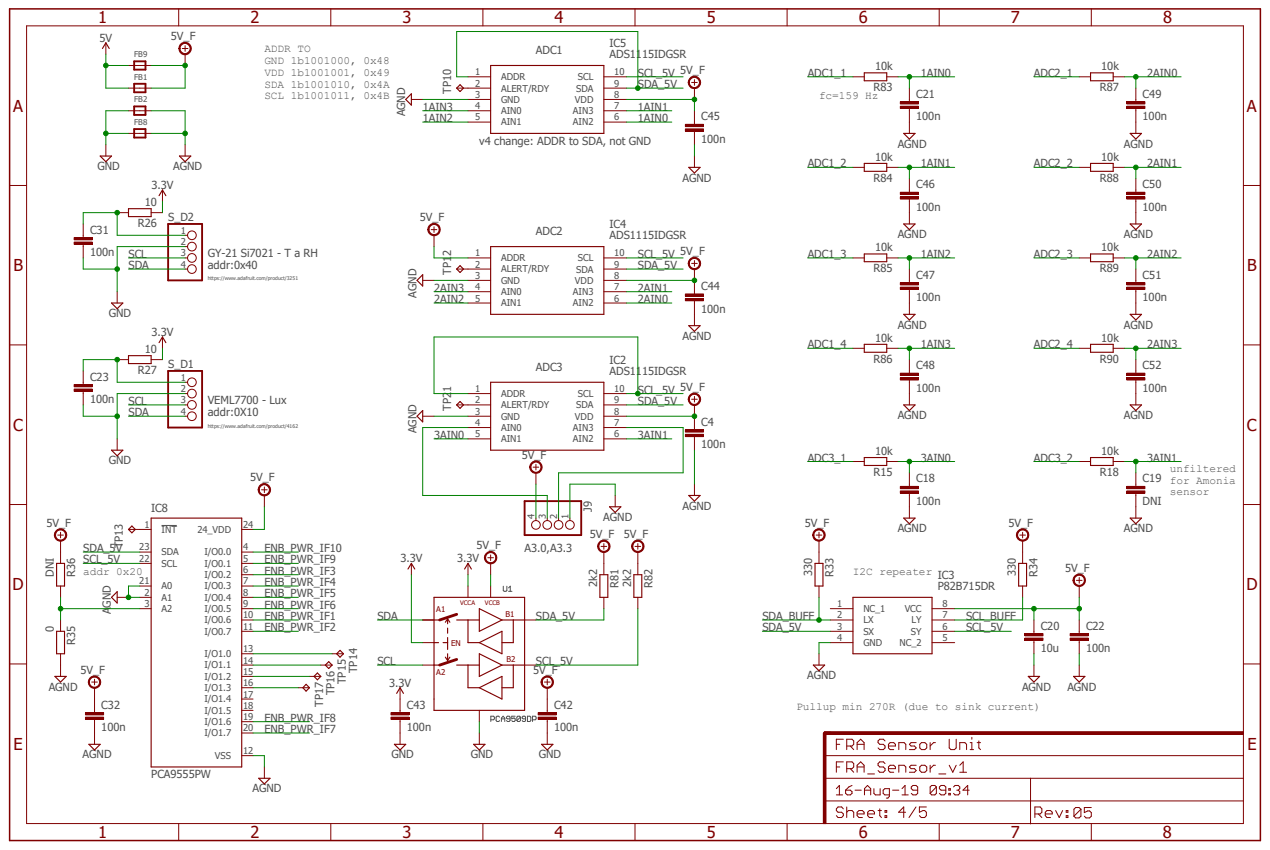
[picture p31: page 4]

https://www.adafruit.com/product/3251

https://www.adafruit.com/product/4162

Pullup min 270R (due to sink current)

# 5V_F ¹³

SCL_BUFF ABCDE | 1 | 2 | 3 | 4 | 5 | 6 | 7 | 8 | ABCDE 1 | 2 | 3 | 4 | 5 | 6 | 7 | 8

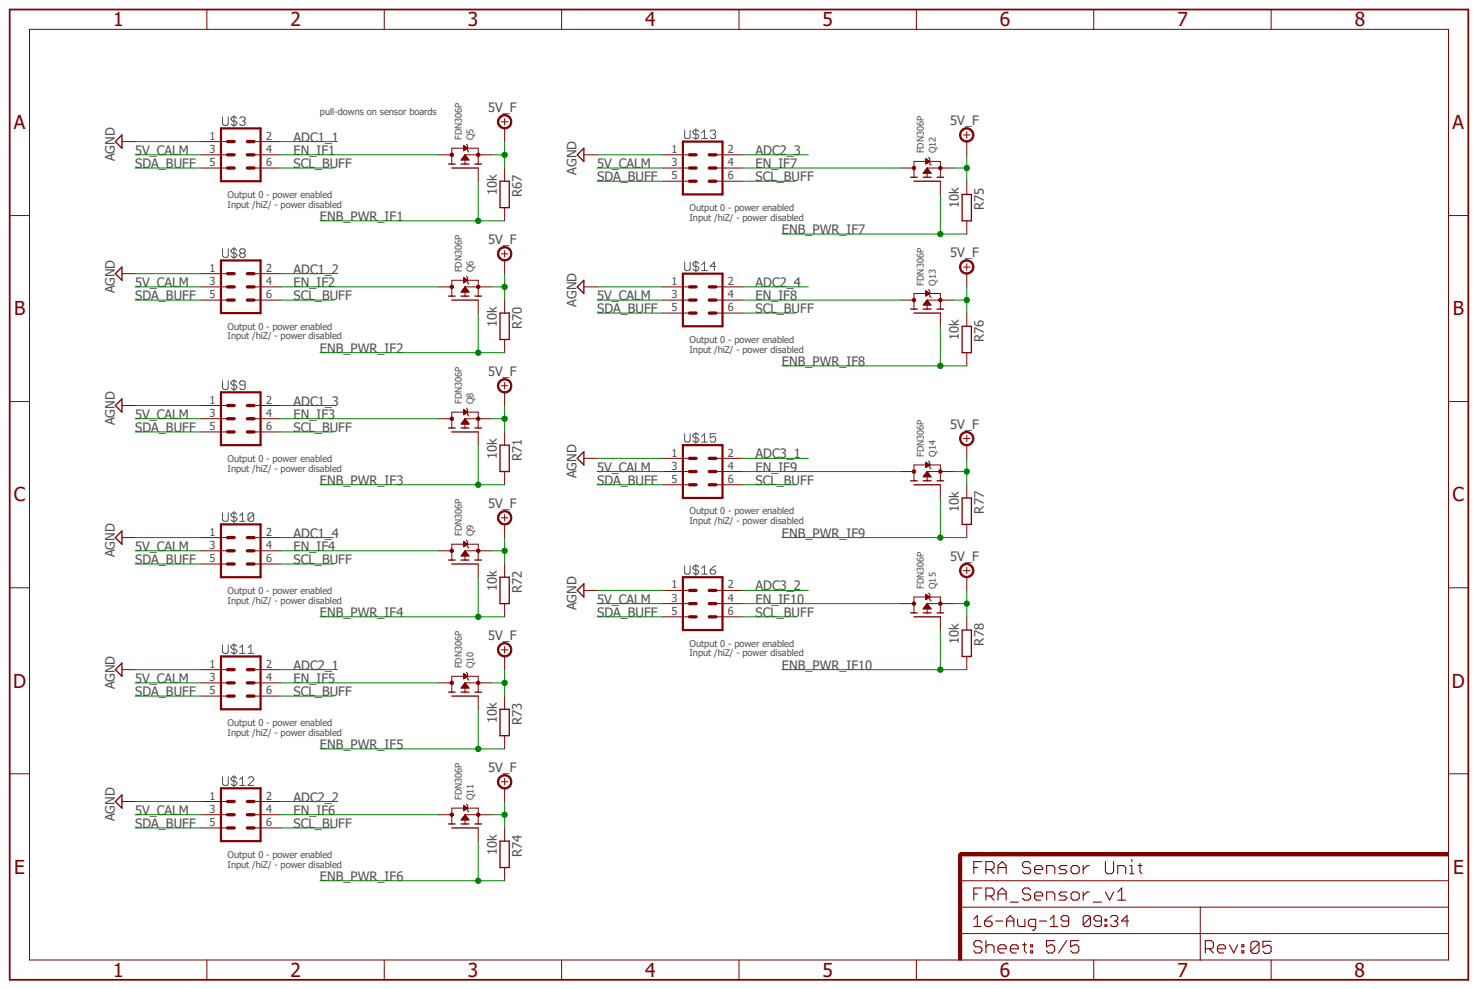
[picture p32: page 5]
pull-downs on sensor boards AGND; FDN³⁰⁶P; 10k AGND; AGND; R⁶⁷ 13; R⁷⁰ 13; R⁷¹ 13; R⁷² 13; Q¹⁰; R⁷³ 13; Q¹¹; R⁷⁴; Q¹²; R⁷⁵ 13; Q¹³; R⁷⁶ 13; Q¹⁴; R⁷⁷ 13; Q¹⁵; R⁷⁸; ADC1_1; 5V_CALM; ENB_PWR_IF1; ADC1_2 EN_IF2; ENB_PWR_IF2; ADC1_3 EN_IF3; ENB_PWR_IF3; ENB_PWR_IF4; ADC1_4; ADC2_1 EN_IF5; ENB_PWR_IF5; ENB_PWR_IF6; ADC2_2; ADC2_3; ADC2_4; ADC3_1; ADC3_2; ENB_PWR_IF10; ENB_PWR_IF9; ENB_PWR_IF8; ENB_PWR_IF7; SDA_BUFF; SCL_BUFF

Output 0 - power enabled
Input /hiZ/ - power disabled

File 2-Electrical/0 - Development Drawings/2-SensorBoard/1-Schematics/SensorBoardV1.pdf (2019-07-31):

A

A

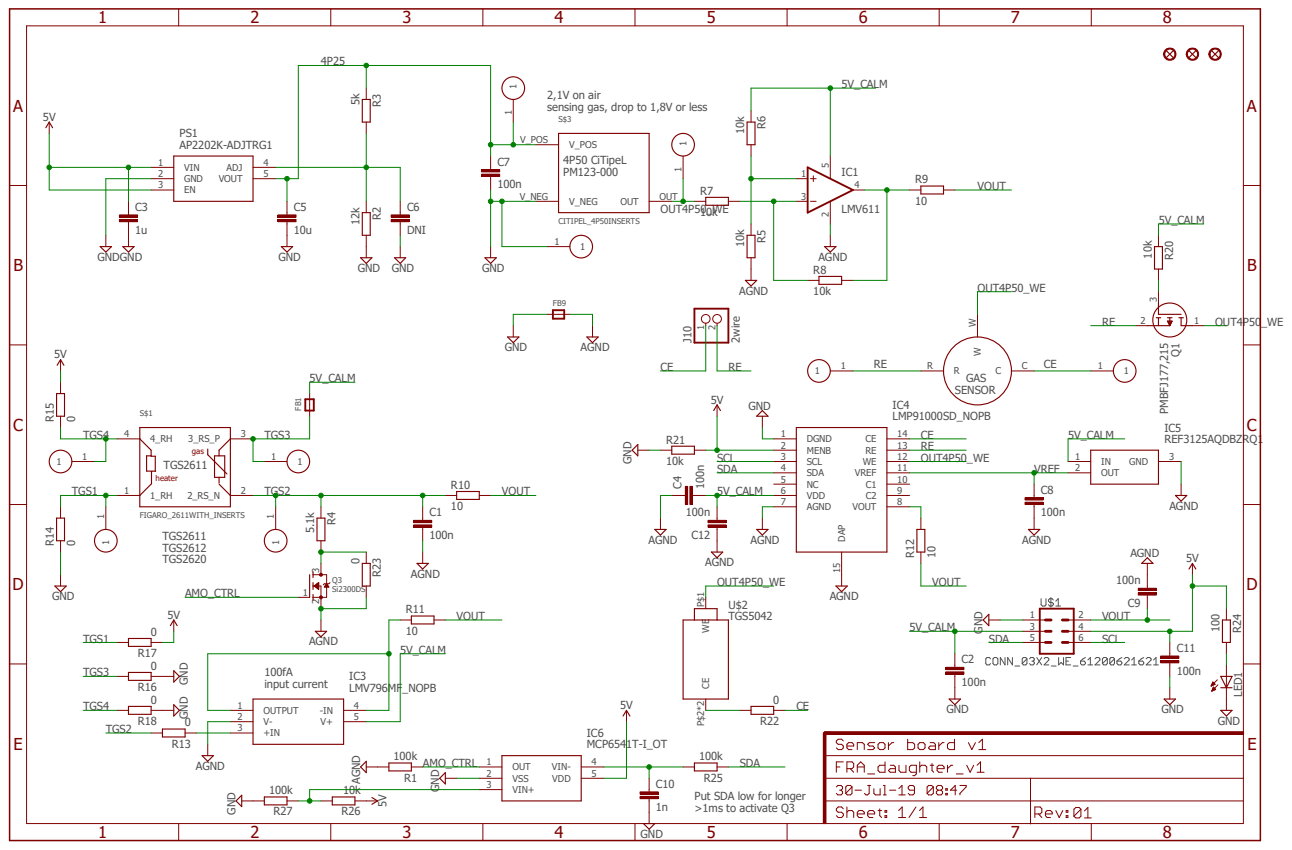
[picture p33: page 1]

2,1V on air
sensing gas, drop to 1,8V or less

Put SDA low for longer
>1ms to activate Q3

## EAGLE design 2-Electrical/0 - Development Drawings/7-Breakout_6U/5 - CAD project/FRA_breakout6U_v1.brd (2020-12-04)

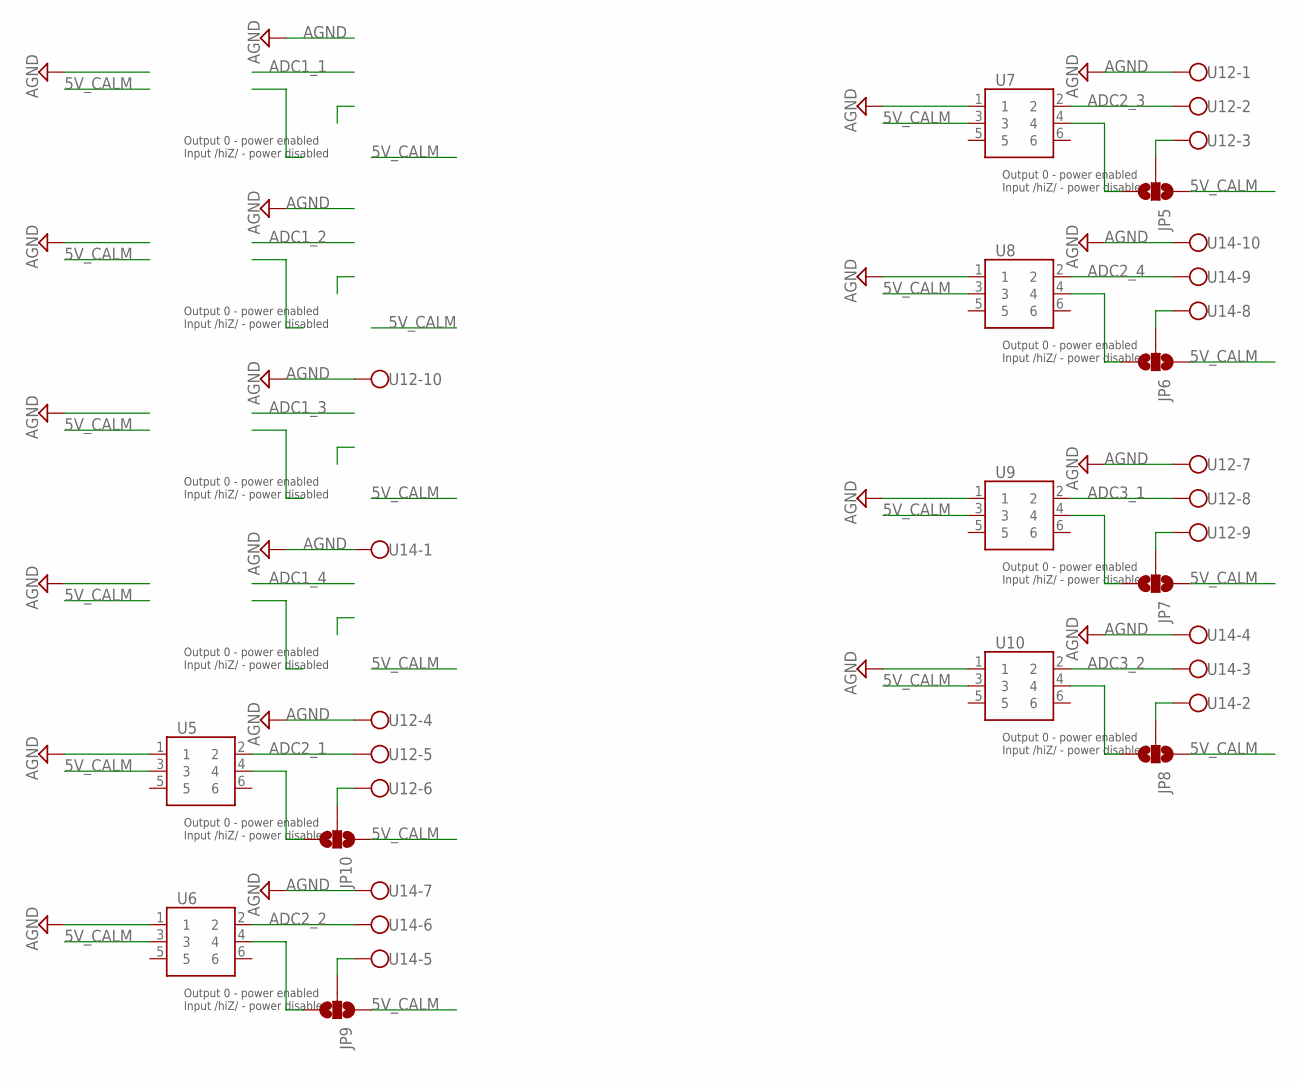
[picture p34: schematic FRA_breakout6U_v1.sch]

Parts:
JP5, JP6, JP7, JP8, JP9, JP10: JUMPER-SMT_3_NO_NO_SILK; SMT-JUMPER_3_0-NO_TRACE_NO-SILK
U5, U6, U7, U8, U9, U10: SSW-103-01-F-D; SHDR6W79P254_2X3_813X495X851P; PARTNO 61200621621
U12, U14: TB003V-500-P10BE

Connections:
5V_CALM: JP5.1, JP6.1, JP7.1, JP8.1, JP9.1, JP10.1, U5.3, U6.3, U7.3, U8.3, U9.3, U10.3
ADC2_1: U5.2, U12.5
ADC2_2: U6.2, U14.6
ADC2_3: U7.2, U12.2
ADC2_4: U8.2, U14.9
ADC3_1: U9.2, U12.8
ADC3_2: U10.2, U14.3
AGND: U5.1, U6.1, U7.1, U8.1, U9.1, U10.1, U12.1, U12.4, U12.7, U12.10, U14.1, U14.4, U14.7, U14.10
unnamed: JP5.2, U12.3
unnamed: JP5.3, U7.4
unnamed: JP6.2, U14.8
unnamed: JP6.3, U8.4
unnamed: JP7.2, U12.9
unnamed: JP7.3, U9.4
unnamed: JP8.2, U14.2
unnamed: JP8.3, U10.4
unnamed: JP9.2, U14.5
unnamed: JP9.3, U6.4
unnamed: JP10.2, U12.6
unnamed: JP10.3, U5.4

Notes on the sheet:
Output 0 - power enabled Input /hiZ/ - power disabled

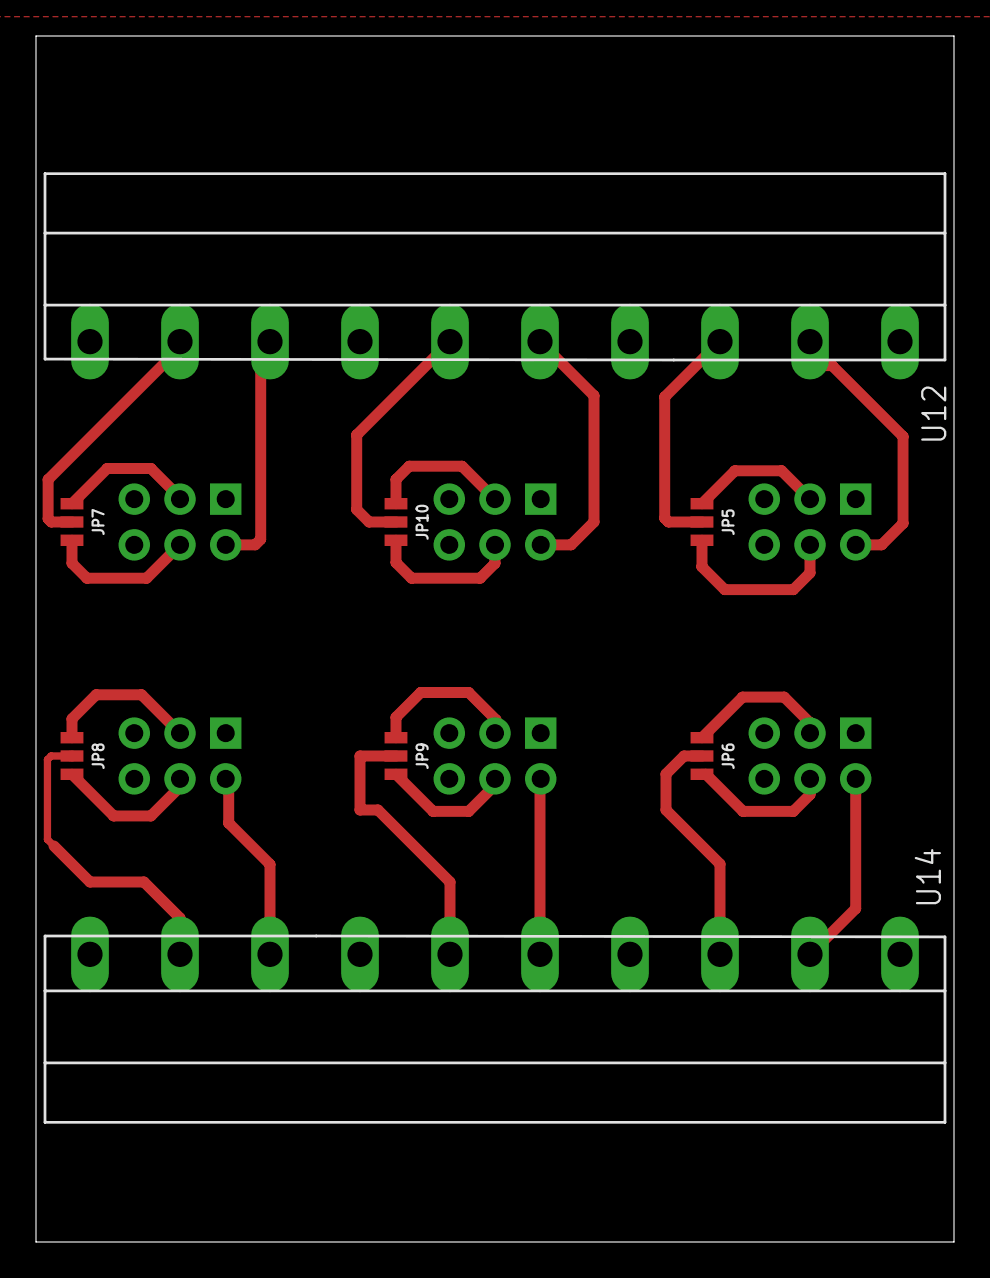
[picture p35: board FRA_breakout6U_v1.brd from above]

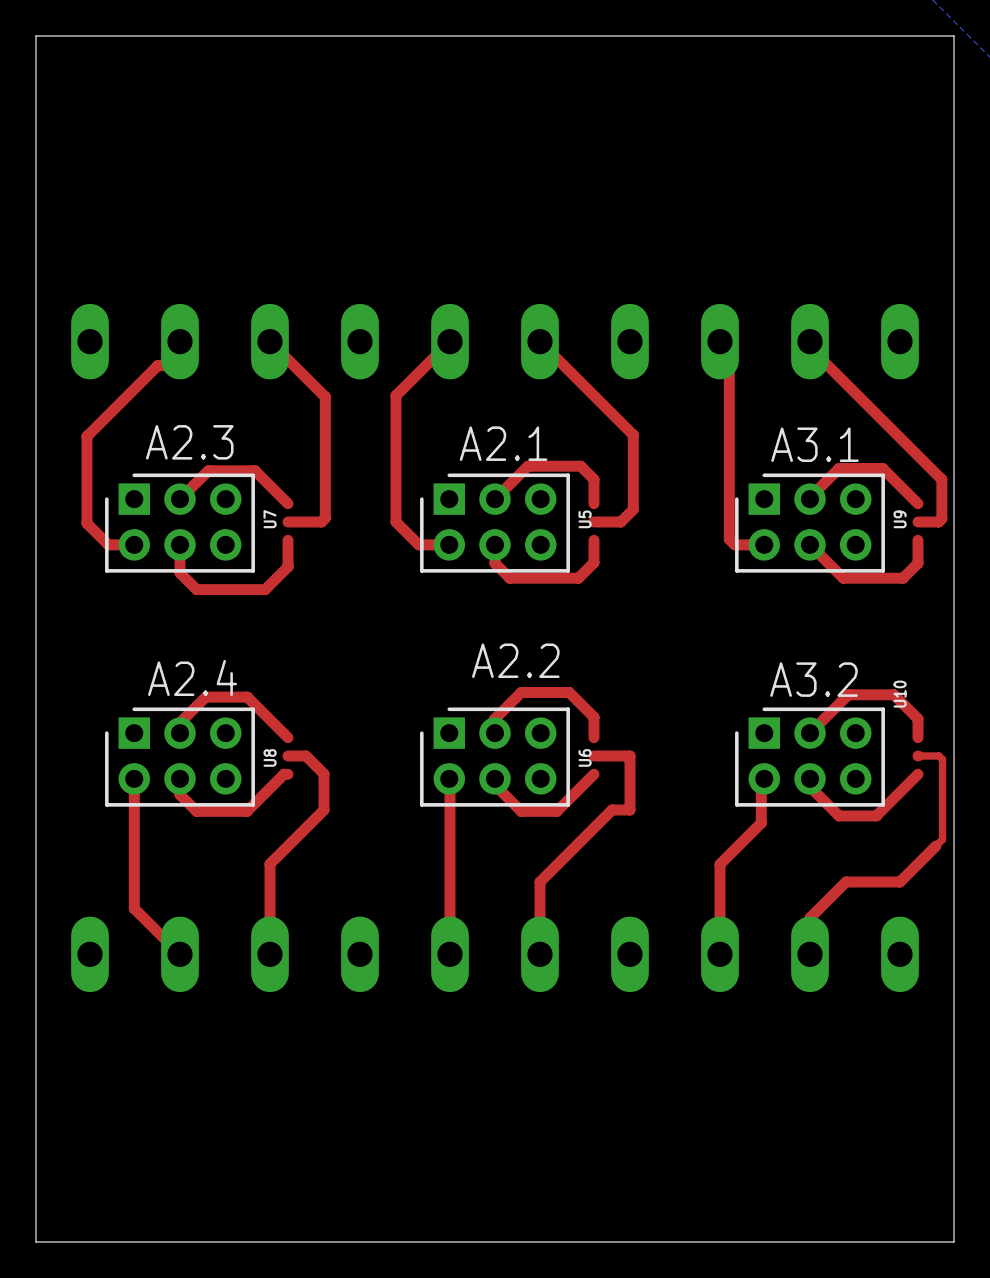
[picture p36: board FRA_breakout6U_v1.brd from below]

Board: 2 copper layers, 51.0 x 67.0 mm, 14 parts (6 on the bottom side), 20 nets.

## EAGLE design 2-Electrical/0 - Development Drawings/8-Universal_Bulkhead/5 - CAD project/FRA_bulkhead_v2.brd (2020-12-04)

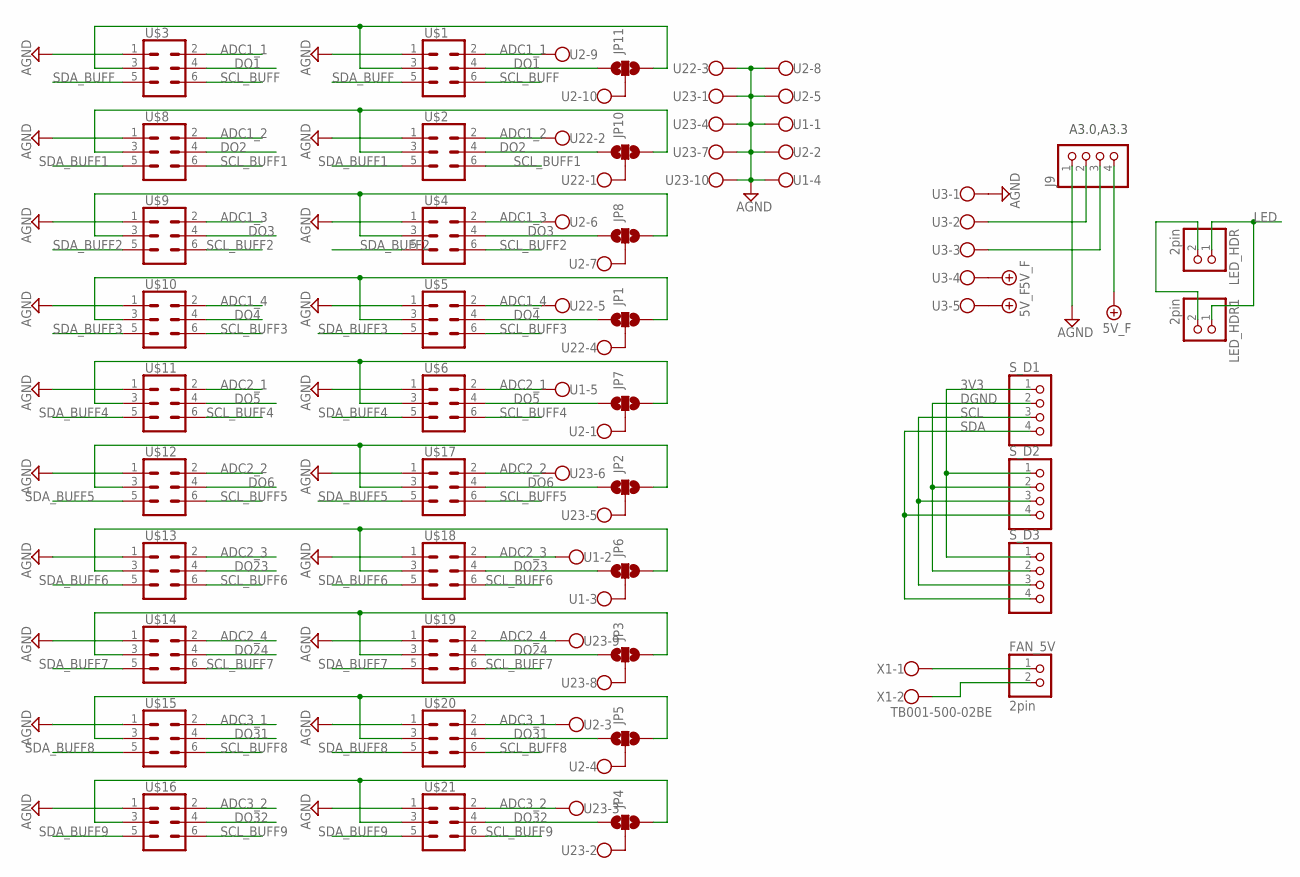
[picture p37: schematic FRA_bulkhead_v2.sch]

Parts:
FAN_5V: 2pin; 1X02; PARTNO TSW-102-07-G-S
J9: 4pin; 1X04; PARTNO 61300411121
JP1, JP2, JP3, JP4, JP5, JP6, JP7, JP8, JP10, JP11: JUMPER-SMT_3_NO_NO_SILK; SMT-JUMPER_3_0-NO_TRACE_NO-SILK
LED_HDR, LED_HDR1: 2pin; 1X02; PARTNO TSW-102-07-G-S
S_D1, S_D2, S_D3: 4pin; 1X04; PARTNO 61300411121
U1, U3, U22: TB003V-500-P05BERIGHTANGLE-NORMAL; TB003-500-P05BE
U2, U23: TB003V-500-P10BERIGHTANGLE-NORMAL; TB003-500-P10BE
U$1, U$2, U$3, U$4, U$5, U$6, U$8, U$9, U$10, U$11, U$12, U$13, U$14, U$15, U$16, U$17, U$18, U$19, U$20, U$21: CONN_03X2_WE_61200621621; WE_61200621621; PARTNO 61200621621
X1: TB001-500-02BE; W237-102; PARTNO TB001-500-02BE

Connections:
3V3: S_D1.1, S_D2.1, S_D3.1
+5V/1: J9.4, U3.4, U3.5
ADC1_1: U2.9, U$1.2, U$3.2
ADC1_2: U22.2, U$2.2, U$8.2
ADC1_3: U2.6, U$4.2, U$9.2
ADC1_4: U22.5, U$5.2, U$10.2
ADC2_1: U1.5, U$6.2, U$11.2
ADC2_2: U23.6, U$12.2, U$17.2
ADC2_3: U1.2, U$13.2, U$18.2
ADC2_4: U23.9, U$14.2, U$19.2
ADC3_1: U2.3, U$15.2, U$20.2
ADC3_2: U23.3, U$16.2, U$21.2
AGND: J9.1, U1.1, U1.4, U2.2, U2.5, U2.8, U3.1, U22.3, U23.1, U23.4, U23.7, U23.10, U$1.1, U$2.1, U$3.1, U$4.1, U$5.1, U$6.1, U$8.1, U$9.1, U$10.1, U$11.1, U$12.1, U$13.1, U$14.1, U$15.1, U$16.1, U$17.1, U$18.1, U$19.1, U$20.1, U$21.1
DGND: S_D1.2, S_D2.2, S_D3.2
DO1: JP11.1, U$1.4, U$3.4
DO2: JP10.1, U$2.4, U$8.4
DO3: JP8.1, U$4.4, U$9.4
DO4: JP1.1, U$5.4, U$10.4
DO5: JP7.1, U$6.4, U$11.4
DO6: JP2.1, U$12.4, U$17.4
DO23: JP6.1, U$13.4, U$18.4
DO24: JP3.1, U$14.4, U$19.4
DO31: JP5.1, U$15.4, U$20.4
DO32: JP4.1, U$16.4, U$21.4
LED: LED_HDR.1, LED_HDR1.1
unnamed: FAN_5V.1, X1.1
unnamed: FAN_5V.2, X1.2
unnamed: JP1.2, U22.4
unnamed: JP2.2, U23.5
unnamed: JP3.2, U23.8
unnamed: JP4.2, U23.2
unnamed: JP10.2, U22.1
unnamed: JP11.2, U2.10
unnamed: JP8.2, U2.7
unnamed: JP5.2, U2.4
unnamed: JP7.2, U2.1
unnamed: JP6.2, U1.3
unnamed: JP11.3, U$1.3, U$3.3
unnamed: J9.3, U3.3
unnamed: JP10.3, U$2.3, U$8.3
unnamed: J9.2, U3.2
unnamed: JP8.3, U$4.3, U$9.3
unnamed: JP1.3, U$5.3, U$10.3
unnamed: JP7.3, U$6.3, U$11.3
unnamed: JP2.3, U$12.3, U$17.3
unnamed: JP6.3, U$13.3, U$18.3
unnamed: JP3.3, U$14.3, U$19.3
unnamed: JP5.3, U$15.3, U$20.3
unnamed: JP4.3, U$16.3, U$21.3
unnamed: LED_HDR.2, LED_HDR1.2
SCL: S_D1.3, S_D2.3, S_D3.3
SCL_BUFF: U$1.6, U$3.6
SCL_BUFF1: U$2.6, U$8.6
SCL_BUFF2: U$4.6, U$9.6
SCL_BUFF3: U$5.6, U$10.6
SCL_BUFF4: U$6.6, U$11.6
SCL_BUFF5: U$12.6, U$17.6
SCL_BUFF6: U$13.6, U$18.6
SCL_BUFF7: U$14.6, U$19.6
SCL_BUFF8: U$15.6, U$20.6
SCL_BUFF9: U$16.6, U$21.6
SDA: S_D1.4, S_D2.4, S_D3.4
SDA_BUFF: U$1.5, U$3.5
SDA_BUFF1: U$2.5, U$8.5
SDA_BUFF2: U$4.5, U$9.5
SDA_BUFF3: U$5.5, U$10.5
SDA_BUFF4: U$6.5, U$11.5
SDA_BUFF5: U$12.5, U$17.5
SDA_BUFF6: U$13.5, U$18.5
SDA_BUFF7: U$14.5, U$19.5
SDA_BUFF8: U$15.5, U$20.5
SDA_BUFF9: U$16.5, U$21.5

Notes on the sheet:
A3.0,A3.3

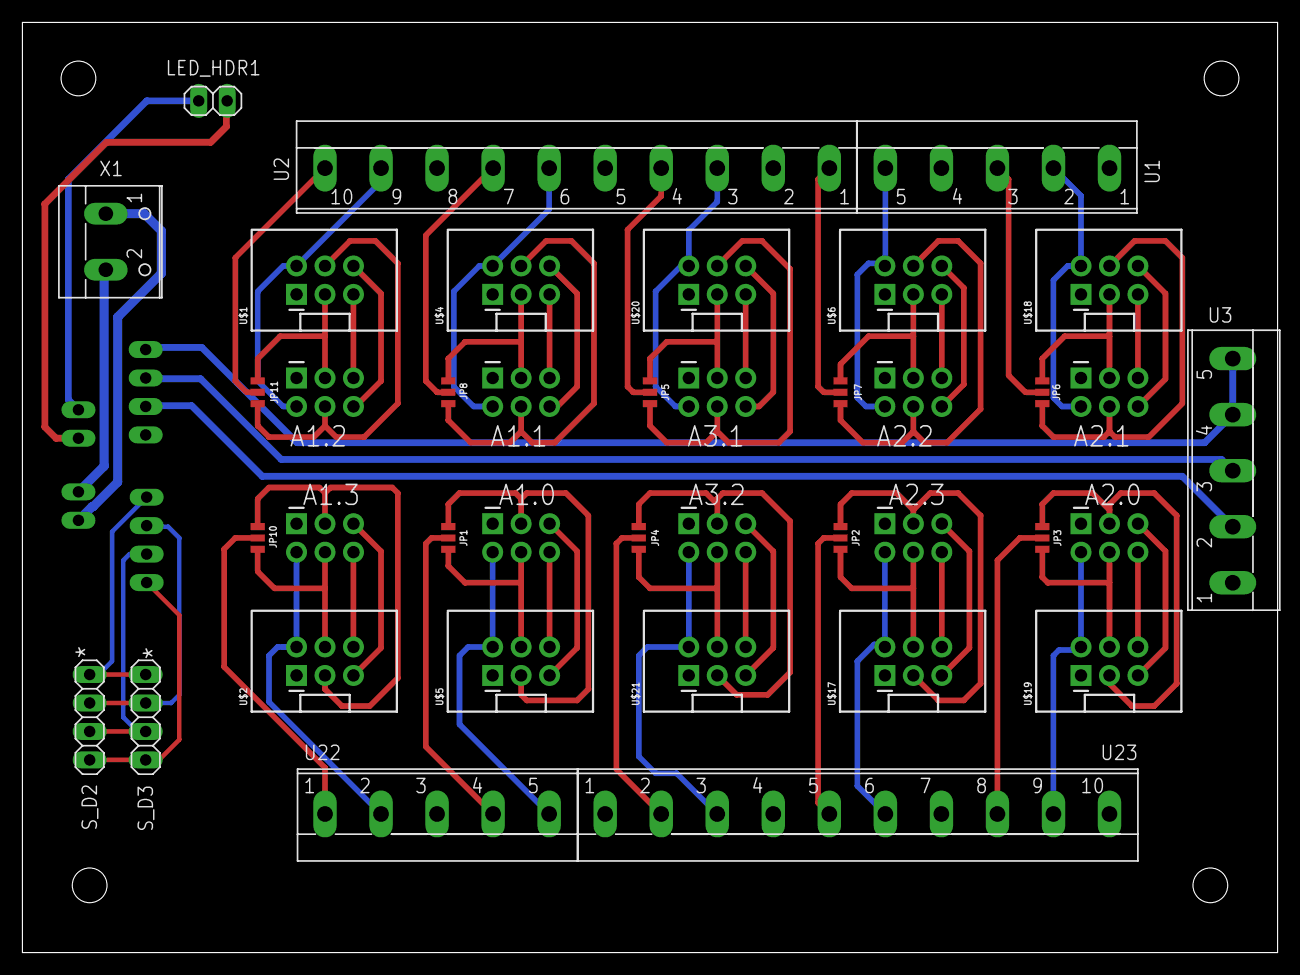
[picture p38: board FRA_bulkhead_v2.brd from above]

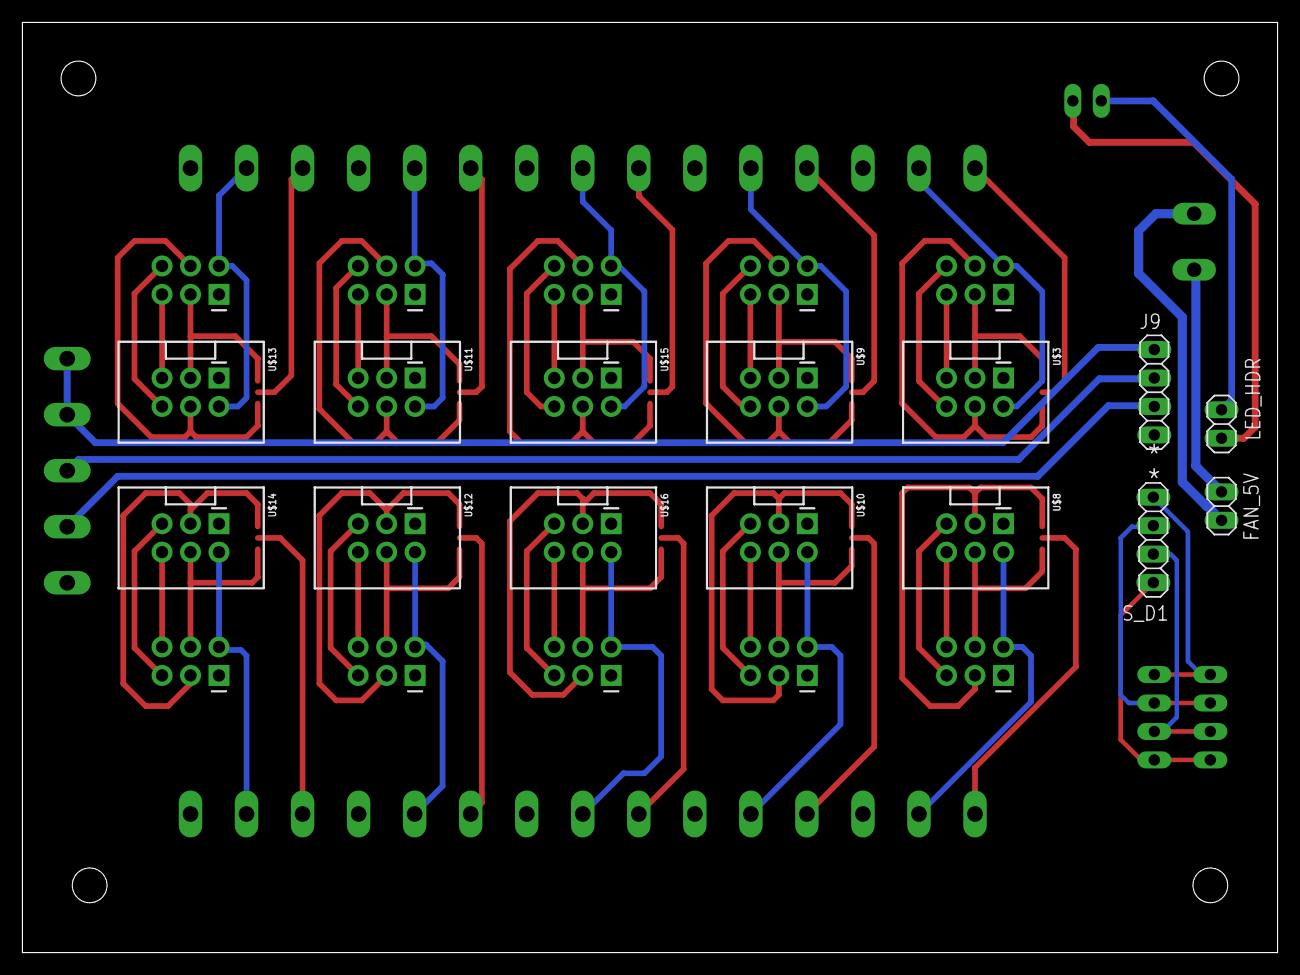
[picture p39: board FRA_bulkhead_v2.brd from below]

Board: 2 copper layers, 112.0 x 83.0 mm, 43 parts (14 on the bottom side), 72 nets.

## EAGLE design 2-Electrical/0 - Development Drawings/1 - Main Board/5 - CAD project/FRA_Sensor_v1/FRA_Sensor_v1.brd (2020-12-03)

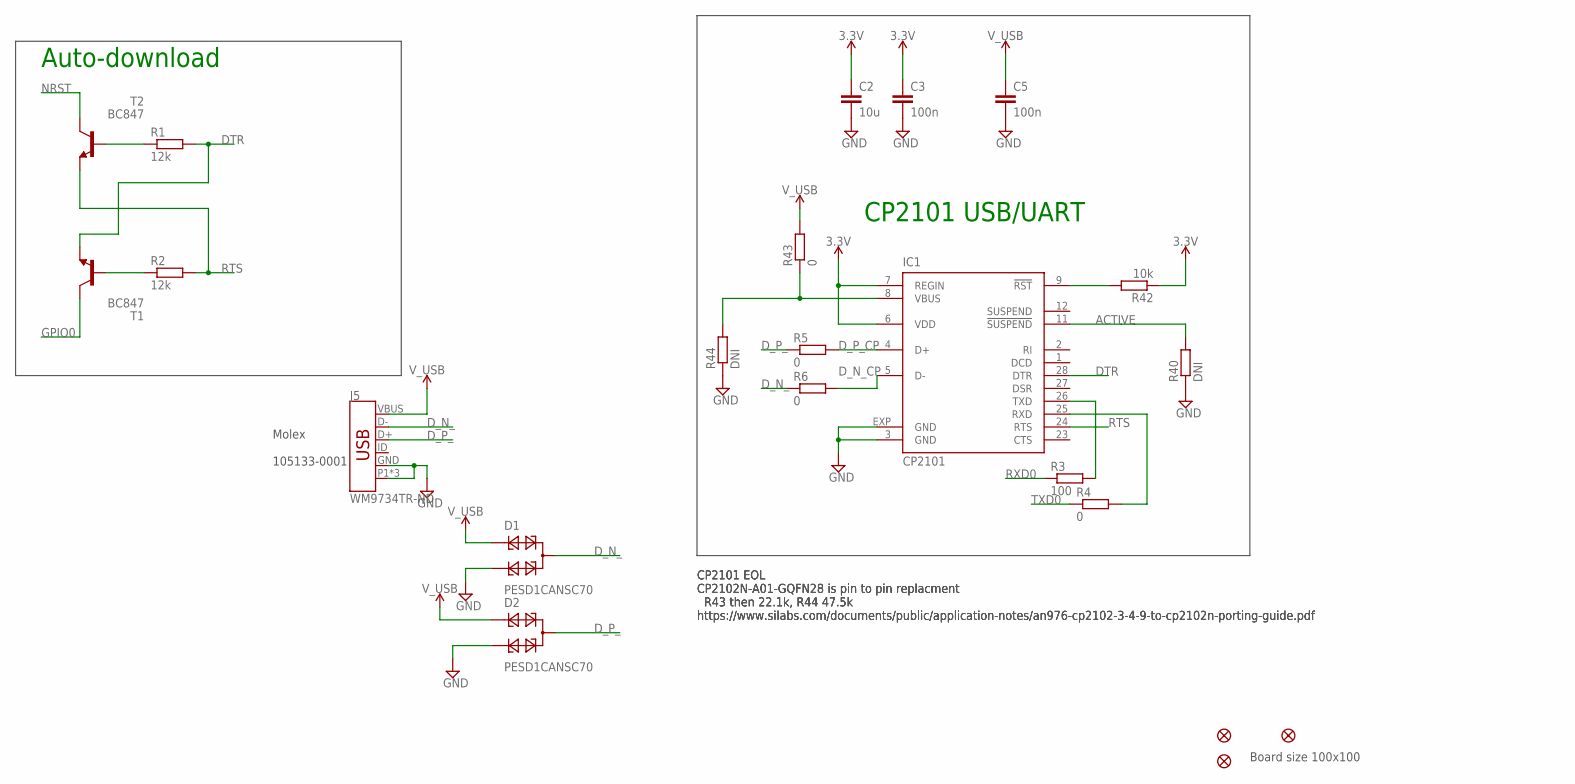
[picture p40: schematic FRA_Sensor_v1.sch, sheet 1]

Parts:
C2: 10u; C0603K; PARTNO GRM188R61A106KE69J
C3, C5: 100n; C0603K; PARTNO CC0603KRX7R8BB104
D1, D2: PESD1CANSC70; SOT323-R; PARTNO PESD1CAN-UX
FID1, FID2, FID4: FIDUCIAL""; FIDUCIAL_1MM
IC1: CP2101; MLP28; PARTNO CP2101-GM
J5: WM9734TR-ND; USB-B-MICRO-SMD_VERT; PARTNO 105133-0001
R1, R2: 12k; R0603; PARTNO RC0603FR-0712KL
R3: 100; R0603; PARTNO CRCW0603100RFKEAC
R4, R5, R6, R43: 0; R0603; PARTNO CRCW06030000Z0EAC
R40, R44: DNI; R0603; PARTNO CRCW06030000Z0EAC
R42: 10k; R0603; PARTNO CRCW060310K0JNEAC
T1, T2: BC847; SOT23; PARTNO BC847A-TP

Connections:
3.3V: C2.1, C3.1, IC1.6 (VDD), IC1.7 (REGIN), R42.1; also elsewhere on the board
ACTIVE: IC1.11 (!SUSPEND), R40.2
DTR: IC1.28 (DTR), R1.2, T1.2 (E)
D_N_: D1.3, J5.D-, R6.1
D_N_CP: IC1.5 (D-), R6.2
D_P_: D2.3, J5.D+, R5.1
D_P_CP: IC1.4 (D+), R5.2
GND: C2.2, C3.2, C5.2, D1.2, D2.2, IC1.3 (GND), IC1.EXP (GND), J5.GND, J5.P1 (SHIELD), J5.P2 (SHIELD), J5.P3 (SHIELD), R40.1, R44.1; also elsewhere on the board
GPIO0: T1.3 (C); also elsewhere on the board
unnamed: R1.1, T2.1 (B)
unnamed: R2.1, T1.1 (B)
unnamed: IC1.9 (!RST), R42.2
unnamed: IC1.8 (VBUS), R43.1, R44.2
NRST: T2.3 (C); also elsewhere on the board
RTS: IC1.24 (RTS), R2.2, T2.2 (E)
RXD0: R3.1; also elsewhere on the board
RXD0_CP2101IN: IC1.26 (TXD), R3.2
TXD0: R4.1; also elsewhere on the board
TXD0_CP2101: IC1.25 (RXD), R4.2
V_USB: C5.1, D1.1, D2.1, J5.VBUS, R43.2

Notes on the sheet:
CP2101 USB/UART
Auto-download
Board size 100x100
Molex 105133-0001
CP2101 EOL CP2102N-A01-GQFN28 is pin to pin replacment R43 then 22.1k, R44 47.5k https://www.silabs.com/documents/public/application-notes/an976-cp2102-3-4-9-to-cp2102n-porting-guide.pdf

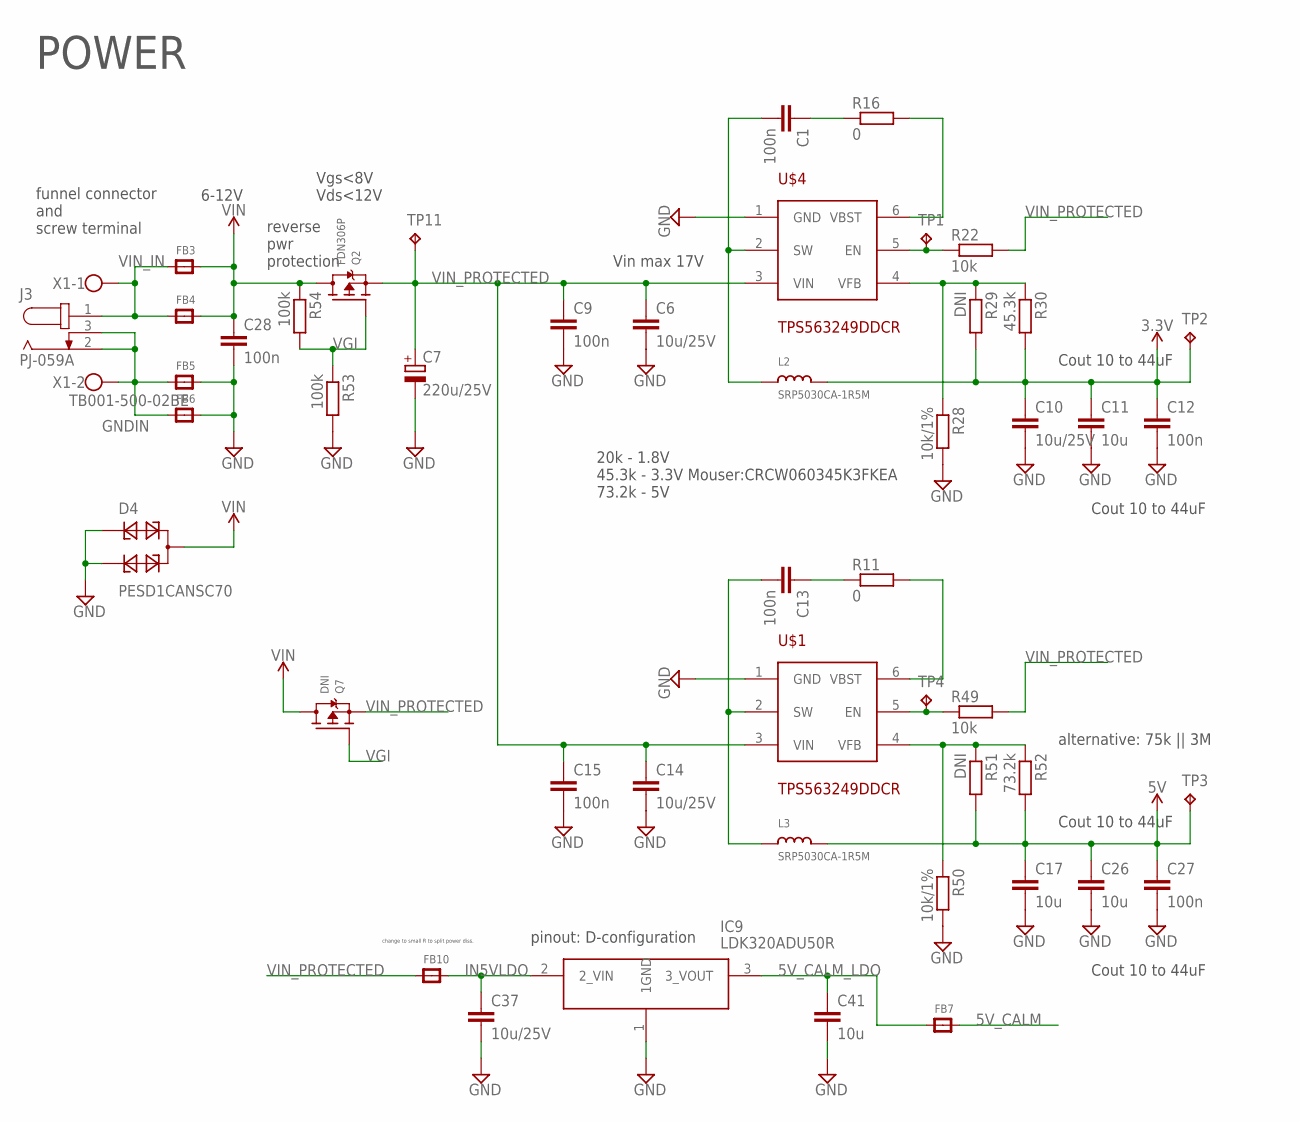
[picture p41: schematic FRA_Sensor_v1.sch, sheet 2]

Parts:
C1, C9, C12, C13, C15, C27, C28: 100n; C0603K; PARTNO CC0603KRX7R8BB104
C6, C10, C14, C37: 10u/25V; C0603K; PARTNO GRM188R61E106KA73J
C7: 220u/25V; 153CLV-0605; PARTNO EMZR250ARA221MF80G
C11, C17, C26, C41: 10u; C0603K; PARTNO GRM188R61A106KE69J
D4: PESD1CANSC70; SOT323-R; PARTNO PESD1CAN-UX
FB3, FB4, FB5, FB6, FB7, FB10: FERRITE; 0603; PARTNO BLM18PG121SN1D
IC9: LDK320ADU50R; ST-SOT-89; PARTNO LDK320ADU50R
J3: PJ-059A; PARTNO PJ-059A
L2, L3: SRP5030CA-1R5M; SRP5030CA; PARTNO SRP5030CA-1R5M
Q2: FDN306P; SOT23-WIDE; PARTNO FDN306P
Q7: DNI; TO252
R11, R16: 0; R0603; PARTNO CRCW06030000Z0EAC
R22, R49: 10k; R0603; PARTNO CRCW060310K0JNEAC
R28, R50: 10k/1%; R0603; PARTNO RN73R1JTTD1002D25
R29, R51: DNI; R0603
R30: 45.3k; R0603; PARTNO ERJ-PB3D4532V
R52: 73.2k; R0603; PARTNO ERJ-PB3D7322V
R53, R54: 100k; R0603; PARTNO CRCW0603100KFKEAC
TP1, TP2, TP3, TP4, TP11: TPTP10R; TP10R
U$1, U$4: TPS563249DDCR; SOT23-6; PARTNO TPS563249DDCR
X1: TB001-500-02BE; W237-102; PARTNO TB001-500-02BE

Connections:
3.3V: C10.1, C11.1, C12.1, L2.P$2 (2), R29.2, R30.2, TP2.TP; also elsewhere on the board
5V: C17.1, C26.1, C27.1, L3.P$2 (2), R51.2, R52.2, TP3.TP; also elsewhere on the board
5V_CALM: FB7.2; also elsewhere on the board
5V_CALM_LDO: C41.1, FB7.1, IC9.3 (3_VOUT)
GND: C6.2, C7.-, C9.2, C10.2, C11.2, C12.2, C14.2, C15.2, C17.2, C26.2, C27.2, C28.2, C37.2, C41.2, D4.1, D4.2, FB5.2, FB6.2, IC9.1 (1GND), R28.2, R50.2, R53.2, U$1.1 (GND), U$4.1 (GND); also elsewhere on the board
GNDIN: FB5.1, FB6.1, J3.2, J3.3, X1.2
IN5VLDO: C37.1, FB10.2, IC9.2 (2_VIN)
unnamed: C1.1, R16.1
unnamed: C13.1, R11.1
unnamed: R16.2, U$4.6 (VBST)
unnamed: C1.2, L2.P$1 (1), U$4.2 (SW)
unnamed: R11.2, U$1.6 (VBST)
unnamed: C13.2, L3.P$1 (1), U$1.2 (SW)
unnamed: R49.1, TP4.TP, U$1.5 (EN)
unnamed: R22.1, TP1.TP, U$4.5 (EN)
unnamed: R28.1, R29.1, R30.1, U$4.4 (VFB)
unnamed: R50.1, R51.1, R52.1, U$1.4 (VFB)
VGI: Q2.1 (G), Q7.1 (G), R53.1, R54.2
VIN: C28.1, D4.3, FB3.2, FB4.2, Q2.3 (D), Q7.3 (D), R54.1
VIN_IN: FB3.1, FB4.1, J3.1, X1.1
VIN_PROTECTED: C6.1, C7.+, C9.1, C14.1, C15.1, FB10.1, Q2.2 (S), Q7.2 (S), R22.2, R49.2, TP11.TP, U$1.3 (VIN), U$4.3 (VIN)

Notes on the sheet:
POWER
20k - 1.8V 45.3k - 3.3V Mouser:CRCW060345K3FKEA 73.2k - 5V
Cout 10 to 44uF
reverse pwr protection
Vgs<8V Vds<12V
6-12V
Vin max 17V
funnel connector and screw terminal
change to small R to split power diss.
pinout: D-configuration
alternative: 75k || 3M

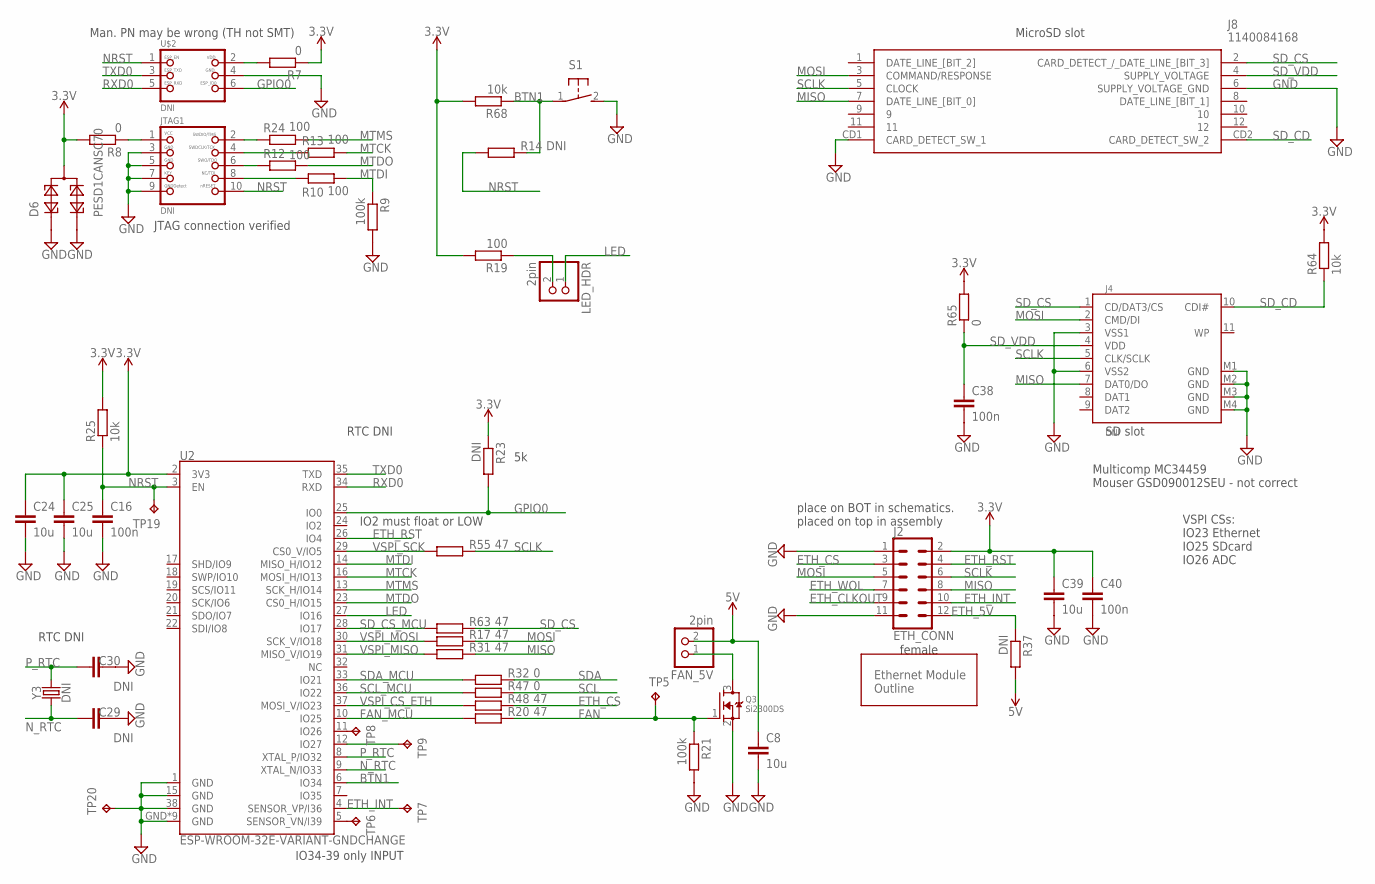
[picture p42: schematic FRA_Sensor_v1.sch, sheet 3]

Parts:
C8, C24, C25, C39: 10u; C0603K; PARTNO GRM188R61A106KE69J
C16, C38, C40: 100n; C0603K; PARTNO CC0603KRX7R8BB104
C29, C30: DNI; C0402; PARTNO C0402C220J5GAC7411
D6: PESD1CANSC70; SOT323-R; PARTNO PESD1CAN-UX
FAN_5V: 2pin; 1X02; PARTNO TSW-102-07-G-S
J2: ETH_CONN; 2X6; PARTNO CES-106-01-T-D
J4: DNI; SDCMF-10915W010; PARTNO GSD090012SEU
J8: 1140084168; PARTNO 1140084168
JTAG1: DNI; 2X05_1.27MM_SMT; PARTNO M50-3600542R
LED_HDR: 2pin; 1X02; PARTNO TSW-102-07-G-S
Q3: Si2300DS; SOT23; PARTNO SI2300DS-T1-GE3
R7, R8, R32, R47, R65: 0; R0603; PARTNO CRCW06030000Z0EAC
R9, R21: 100k; R0603; PARTNO CRCW0603100KFKEAC
R10, R12, R13, R19, R24: 100; R0603; PARTNO CRCW0603100RFKEAC
R14, R23, R37: DNI; R0603; PARTNO CRCW06030000Z0EAC
R17, R20, R31, R48, R55, R63: 47; R0603; PARTNO CRCW060347R0FKEAC
R25, R64, R68: 10k; R0603; PARTNO CRCW060310K0JNEAC
S1: 31-XX; B3F-31XX; PARTNO FSMRA5JH
TP5, TP6, TP7, TP8, TP9, TP19, TP20: TPTP10R; TP10R
U2: ESP-WROOM-32E-VARIANT-GNDCHANGE; ESP-WROOM-32E; PARTNO ESP32-WROOM-32
U$2: DNI; 2X03_1.27MM_SMT; PARTNO HTMS-103-03-T-D-SM
U$7: ETH_MODULE_OUTLINE; ETH_MODULE_OUTLINE_SMALL
Y3: DNI; CRYSTAL-SMD-3.2X1.5MM; PARTNO FC-135 32.7680KA-A3

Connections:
3.3V: C24.1, C25.1, C39.1, C40.1, D6.3, J2.2, R7.1, R8.2, R19.2, R23.1, R25.2, R64.2, R65.2, R68.2, U2.2 (3V3); also elsewhere on the board
5V: C8.1, FAN_5V.2, R37.2; also elsewhere on the board
BTN1: R14.2, R68.1, S1.1, U2.6 (IO34)
ETH_5V: J2.12, R37.1
ETH_CLKOUT: J2.9
ETH_CS: J2.3, R48.2
ETH_INT: J2.10, TP7.TP, U2.4 (SENSOR_VP/I36)
ETH_RST: J2.4, U2.26 (IO4)
ETH_WOL: J2.7
FAN: Q3.1 (G), R20.2, R21.1, TP5.TP
FAN_MCU: R20.1, U2.10 (IO25)
GND: C8.2, C16.2, C24.2, C25.2, C29.2, C30.2, C38.2, C39.2, C40.2, D6.1, D6.2, J2.1, J2.11, J4.3 (VSS1), J4.6 (VSS2), J4.M1 (GND), J4.M2 (GND), J4.M3 (GND), J4.M4 (GND), J8.6 (SUPPLY_VOLTAGE_GND), J8.CD1 (CARD_DETECT_SW_1), JTAG1.3, JTAG1.5, JTAG1.7, JTAG1.9, Q3.2 (S), R9.2, R21.2, S1.2 (S), TP20.TP, U2.1 (GND), U2.15 (GND), U2.38 (GND), U2.GND, U2.GND1 (GND), U2.GND2 (GND), U2.GND3 (GND), U2.GND4 (GND), U2.GND5 (GND), U2.GND6 (GND), U2.GND7 (GND), U2.GND8 (GND), U$2.4; also elsewhere on the board
GPIO0: R23.2, U2.25 (IO0), U$2.6; also elsewhere on the board
LED: LED_HDR.1, U2.27 (IO16)
MISO: J2.8, J4.7 (DAT0/DO), J8.7 (DATE_LINE_[BIT_0]), R31.2
MOSI: J2.5, J4.2 (CMD/DI), J8.3 (COMMAND/RESPONSE), R17.2
MTCK: R13.2, U2.16 (MOSI_H/IO13)
MTDI: R9.1, R10.2, U2.14 (MISO_H/IO12)
MTDO: R12.2, U2.23 (CS0_H/IO15)
MTMS: R24.2, U2.13 (SCK_H/IO14)
unnamed: LED_HDR.2, R19.1
unnamed: FAN_5V.1, Q3.3 (D)
unnamed: TP6.TP, U2.5 (SENSOR_VN/I39)
unnamed: TP8.TP, U2.11 (IO26)
unnamed: TP9.TP, U2.12 (IO27)
NRST: C16.1, JTAG1.10, R14.1, R25.1, TP19.TP, U2.3 (EN), U$2.1; also elsewhere on the board
N_RTC: C29.1, U2.9 (XTAL_N/IO33), Y3.P$1 (1)
P_RTC: C30.1, U2.8 (XTAL_P/IO32), Y3.P$2 (2)
RXD0: U2.34 (RXD), U$2.5; also elsewhere on the board
SCL: R47.2; also elsewhere on the board
SCLK: J2.6, J4.5 (CLK/SCLK), J8.5 (CLOCK), R55.2
SCL_MCU: R47.1, U2.36 (IO22)
SDA: R32.2; also elsewhere on the board
SDA_MCU: R32.1, U2.33 (IO21)
SD_CD: J4.10 (CDI#), J8.CD2 (CARD_DETECT_SW_2), R64.1
SD_CS: J4.1 (CD/DAT3/CS), J8.2 (CARD_DETECT_/_DATE_LINE_[BIT_3]), R63.2
SD_CS_MCU: R63.1, U2.28 (IO17)
SD_VDD: C38.1, J4.4 (VDD), J8.4 (SUPPLY_VOLTAGE), R65.1
TCKCONN: JTAG1.4, R13.1
TDICONN: JTAG1.8, R10.1
TDOCONN: JTAG1.6, R12.1
TMSCONN: JTAG1.2, R24.1
TXD0: U2.35 (TXD), U$2.3; also elsewhere on the board
VCCJTAG: JTAG1.1, R8.1
VDDPROG: R7.2, U$2.2
VSPI_CS_ETH: R48.1, U2.37 (MOSI_V/IO23)
VSPI_MISO: R31.1, U2.31 (MISO_V/IO19)
VSPI_MOSI: R17.1, U2.30 (SCK_V/IO18)
VSPI_SCK: R55.1, U2.29 (CS0_V/IO5)

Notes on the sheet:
VSPI CSs: IO23 Ethernet IO25 SDcard IO26 ADC
MicroSD slot
SD slot
JTAG connection verified
IO34-39 only INPUT
place on BOT in schematics. placed on top in assembly
female
RTC DNI
Multicomp MC34459 Mouser GSD090012SEU - not correct
IO2 must float or LOW
Man. PN may be wrong (TH not SMT)

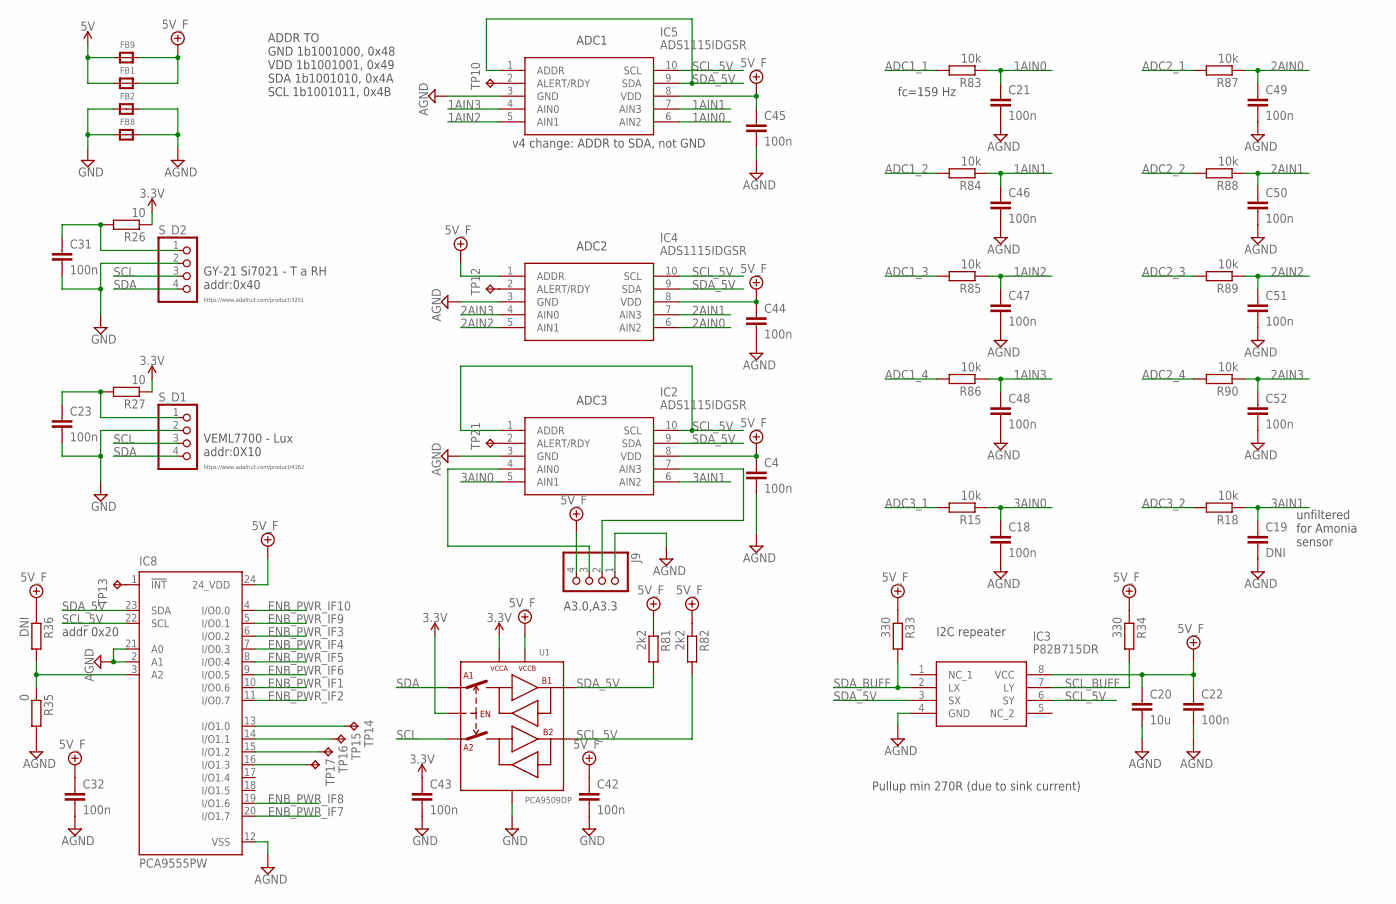
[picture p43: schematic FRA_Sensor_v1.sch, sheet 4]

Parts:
C4, C18, C21, C22, C23, C31, C32, C42, C43, C44, C45, C46, C47, C48, C49, C50, C51, C52: 100n; C0603K; PARTNO CC0603KRX7R8BB104
C19: DNI; C0603K; PARTNO CC0603KRX7R8BB104
C20: 10u; C0603K; PARTNO GRM188R61A106KE69J
FB1, FB2, FB8, FB9: FERRITE; 0603; PARTNO BLM18PG121SN1D
IC2, IC4, IC5: ADS1115IDGSR; SOP50P490X110-10N; PARTNO ADS1115IDGSR
IC3: P82B715DR; SOIC127P600X175-8N; PARTNO P82B715DR
IC8: PCA9555PW; TSSOP24; PARTNO PCA9555PW,118
J9: 4pin; 1X04; PARTNO 61300411121
R15, R18, R83, R84, R85, R86, R87, R88, R89, R90: 10k; R0603; PARTNO CRCW060310K0JNEAC
R26, R27: 10; R0603; PARTNO CRCW060310R0FKEAC
R33, R34: 330; R0603; PARTNO CRCW0603330RFKEAC
R35: 0; R0603; PARTNO CRCW06030000Z0EAC
R36: DNI; R0603; PARTNO CRCW0603330RFKEAC
R81, R82: 2k2; R0603; PARTNO RCS06032K20JNEA
S_D1, S_D2: 4pin; 1X04; PARTNO 61300411121
TP10, TP12, TP13, TP14, TP15, TP16, TP17, TP21: TPTP10R; TP10R
U1: PCA9509DP; SOT505-1; PARTNO PCA9509DP,118

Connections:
1AIN0: C21.1, IC5.6 (AIN2), R83.1
1AIN1: C46.1, IC5.7 (AIN3), R84.1
1AIN2: C47.1, IC5.5 (AIN1), R85.1
1AIN3: C48.1, IC5.4 (AIN0), R86.1
2AIN0: C49.1, IC4.6 (AIN2), R87.1
2AIN1: C50.1, IC4.7 (AIN3), R88.1
2AIN2: C51.1, IC4.5 (AIN1), R89.1
2AIN3: C52.1, IC4.4 (AIN0), R90.1
3.3V: C43.1, R26.1, R27.1, U1.1 (VCC(A)), U1.5 (EN); also elsewhere on the board
3AIN0: C18.1, IC2.5 (AIN1), R15.1
3AIN1: C19.1, IC2.6 (AIN2), R18.1
5V: FB1.1, FB9.1; also elsewhere on the board
+5V/1: C4.1, C20.1, C22.1, C32.1, C42.1, C44.1, C45.1, FB1.2, FB9.2, IC2.8 (VDD), IC3.8 (VCC), IC4.1 (ADDR), IC4.8 (VDD), IC5.8 (VDD), IC8.24 (24_VDD), J9.4, R33.1, R34.1, R36.1, R81.1, R82.1, U1.8 (VCC(B)); also elsewhere on the board
ADC1_1: R83.2; also elsewhere on the board
ADC1_2: R84.2; also elsewhere on the board
ADC1_3: R85.2; also elsewhere on the board
ADC1_4: R86.2; also elsewhere on the board
ADC2_1: R87.2; also elsewhere on the board
ADC2_2: R88.2; also elsewhere on the board
ADC2_3: R89.2; also elsewhere on the board
ADC2_4: R90.2; also elsewhere on the board
ADC3_1: R15.2; also elsewhere on the board
ADC3_2: R18.2; also elsewhere on the board
AGND: C4.2, C18.2, C19.2, C20.2, C21.2, C22.2, C32.2, C44.2, C45.2, C46.2, C47.2, C48.2, C49.2, C50.2, C51.2, C52.2, FB2.2, FB8.2, IC2.3 (GND), IC3.4 (GND), IC4.3 (GND), IC5.3 (GND), IC8.2 (A1), IC8.12 (VSS), IC8.21 (A0), J9.1, R35.2; also elsewhere on the board
ENB_PWR_IF1: IC8.10 (I/O0.6); also elsewhere on the board
ENB_PWR_IF2: IC8.11 (I/O0.7); also elsewhere on the board
ENB_PWR_IF3: IC8.6 (I/O0.2); also elsewhere on the board
ENB_PWR_IF4: IC8.7 (I/O0.3); also elsewhere on the board
ENB_PWR_IF5: IC8.8 (I/O0.4); also elsewhere on the board
ENB_PWR_IF6: IC8.9 (I/O0.5); also elsewhere on the board
ENB_PWR_IF7: IC8.20 (I/O1.7); also elsewhere on the board
ENB_PWR_IF8: IC8.19 (I/O1.6); also elsewhere on the board
ENB_PWR_IF9: IC8.5 (I/O0.1); also elsewhere on the board
ENB_PWR_IF10: IC8.4 (I/O0.0); also elsewhere on the board
GND: C23.2, C31.2, C42.2, C43.2, FB2.1, FB8.1, S_D1.2, S_D2.2, U1.4 (GND); also elsewhere on the board
unnamed: C23.1, R27.2, S_D1.1
unnamed: C31.1, R26.2, S_D2.1
unnamed: IC2.2 (ALERT/RDY), TP21.TP
unnamed: IC8.13 (I/O1.0), TP14.TP
unnamed: IC8.14 (I/O1.1), TP15.TP
unnamed: IC8.15 (I/O1.2), TP16.TP
unnamed: IC8.16 (I/O1.3), TP17.TP
unnamed: IC2.4 (AIN0), J9.3
unnamed: IC2.7 (AIN3), J9.2
unnamed: IC8.3 (A2), R35.1, R36.2
unnamed: IC4.2 (ALERT/RDY), TP12.TP
unnamed: IC5.2 (ALERT/RDY), TP10.TP
unnamed: IC8.1 (!INT), TP13.TP
SCL: S_D1.3, S_D2.3, U1.3 (A2); also elsewhere on the board
SCL_5V: IC2.1 (ADDR), IC2.10 (SCL), IC3.6 (SY), IC4.10 (SCL), IC5.10 (SCL), IC8.22 (SCL), R82.2, U1.6 (B2)
SCL_BUFF: IC3.7 (LY), R34.2; also elsewhere on the board
SDA: S_D1.4, S_D2.4, U1.2 (A1); also elsewhere on the board
SDA_5V: IC2.9 (SDA), IC3.3 (SX), IC4.9 (SDA), IC5.1 (ADDR), IC5.9 (SDA), IC8.23 (SDA), R81.2, U1.7 (B1)
SDA_BUFF: IC3.2 (LX), R33.2; also elsewhere on the board

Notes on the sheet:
VEML7700 - Lux addr:0X10
https://www.adafruit.com/product/4162
https://www.adafruit.com/product/3251
ADDR TO GND 1b1001000, 0x48 VDD 1b1001001, 0x49 SDA 1b1001010, 0x4A SCL 1b1001011, 0x4B
addr 0x20
fc=159 Hz
GY-21 Si7021 - T a RH addr:0x40
Pullup min 270R (due to sink current)
I2C repeater
ADC1
ADC2
ADC3
A3.0,A3.3
v4 change: ADDR to SDA, not GND
unfiltered for Amonia sensor

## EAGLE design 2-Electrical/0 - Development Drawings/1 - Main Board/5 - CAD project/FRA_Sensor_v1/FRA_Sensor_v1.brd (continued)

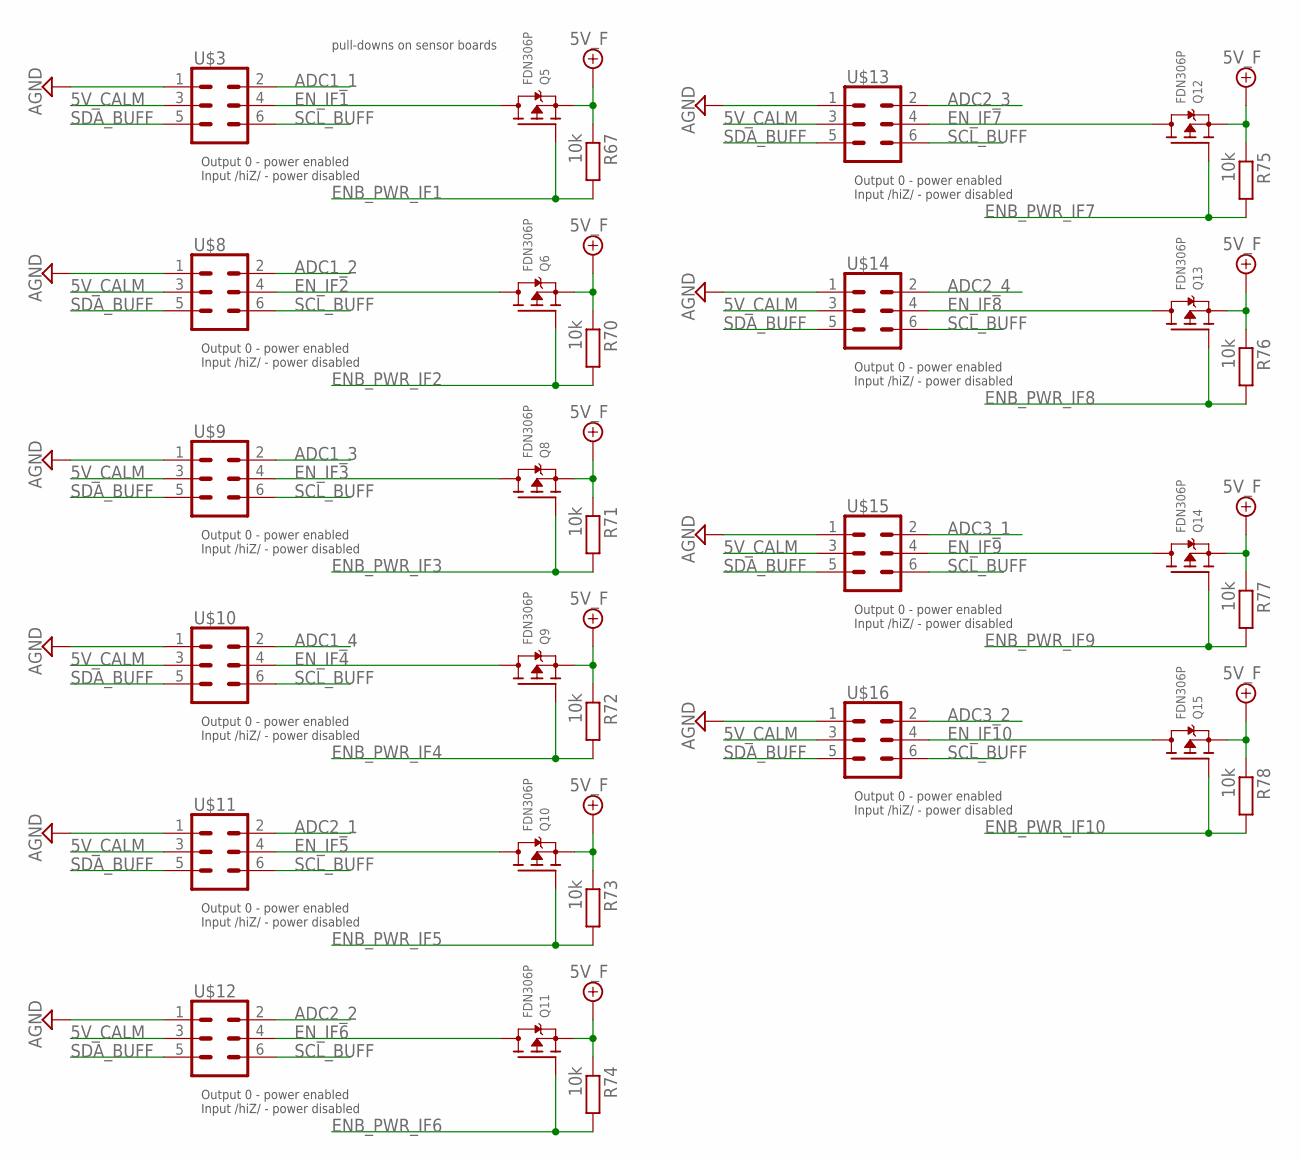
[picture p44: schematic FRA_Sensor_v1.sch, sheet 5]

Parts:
Q5, Q6, Q8, Q9, Q10, Q11, Q12, Q13, Q14, Q15: FDN306P; SOT23-WIDE; PARTNO FDN306P
R67, R70, R71, R72, R73, R74, R75, R76, R77, R78: 10k; R0603; PARTNO CRCW060310K0JNEAC
U$3, U$8, U$9, U$10, U$11, U$12, U$13, U$14, U$15, U$16: CONN_03X2_WE_61200621621; WE_61200621621; PARTNO 61200621621

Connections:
5V_CALM: U$3.3, U$8.3, U$9.3, U$10.3, U$11.3, U$12.3, U$13.3, U$14.3, U$15.3, U$16.3; also elsewhere on the board
+5V/1: Q5.2 (S), Q6.2 (S), Q8.2 (S), Q9.2 (S), Q10.2 (S), Q11.2 (S), Q12.2 (S), Q13.2 (S), Q14.2 (S), Q15.2 (S), R67.1, R70.1, R71.1, R72.1, R73.1, R74.1, R75.1, R76.1, R77.1, R78.1; also elsewhere on the board
ADC1_1: U$3.2; also elsewhere on the board
ADC1_2: U$8.2; also elsewhere on the board
ADC1_3: U$9.2; also elsewhere on the board
ADC1_4: U$10.2; also elsewhere on the board
ADC2_1: U$11.2; also elsewhere on the board
ADC2_2: U$12.2; also elsewhere on the board
ADC2_3: U$13.2; also elsewhere on the board
ADC2_4: U$14.2; also elsewhere on the board
ADC3_1: U$15.2; also elsewhere on the board
ADC3_2: U$16.2; also elsewhere on the board
AGND: U$3.1, U$8.1, U$9.1, U$10.1, U$11.1, U$12.1, U$13.1, U$14.1, U$15.1, U$16.1; also elsewhere on the board
ENB_PWR_IF1: Q5.1 (G), R67.2; also elsewhere on the board
ENB_PWR_IF2: Q6.1 (G), R70.2; also elsewhere on the board
ENB_PWR_IF3: Q8.1 (G), R71.2; also elsewhere on the board
ENB_PWR_IF4: Q9.1 (G), R72.2; also elsewhere on the board
ENB_PWR_IF5: Q10.1 (G), R73.2; also elsewhere on the board
ENB_PWR_IF6: Q11.1 (G), R74.2; also elsewhere on the board
ENB_PWR_IF7: Q12.1 (G), R75.2; also elsewhere on the board
ENB_PWR_IF8: Q13.1 (G), R76.2; also elsewhere on the board
ENB_PWR_IF9: Q14.1 (G), R77.2; also elsewhere on the board
ENB_PWR_IF10: Q15.1 (G), R78.2; also elsewhere on the board
EN_IF1: Q5.3 (D), U$3.4
EN_IF2: Q6.3 (D), U$8.4
EN_IF3: Q8.3 (D), U$9.4
EN_IF4: Q9.3 (D), U$10.4
EN_IF5: Q10.3 (D), U$11.4
EN_IF6: Q11.3 (D), U$12.4
EN_IF7: Q12.3 (D), U$13.4
EN_IF8: Q13.3 (D), U$14.4
EN_IF9: Q14.3 (D), U$15.4
EN_IF10: Q15.3 (D), U$16.4
SCL_BUFF: U$3.6, U$8.6, U$9.6, U$10.6, U$11.6, U$12.6, U$13.6, U$14.6, U$15.6, U$16.6; also elsewhere on the board
SDA_BUFF: U$3.5, U$8.5, U$9.5, U$10.5, U$11.5, U$12.5, U$13.5, U$14.5, U$15.5, U$16.5; also elsewhere on the board

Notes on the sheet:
Output 0 - power enabled Input /hiZ/ - power disabled
pull-downs on sensor boards

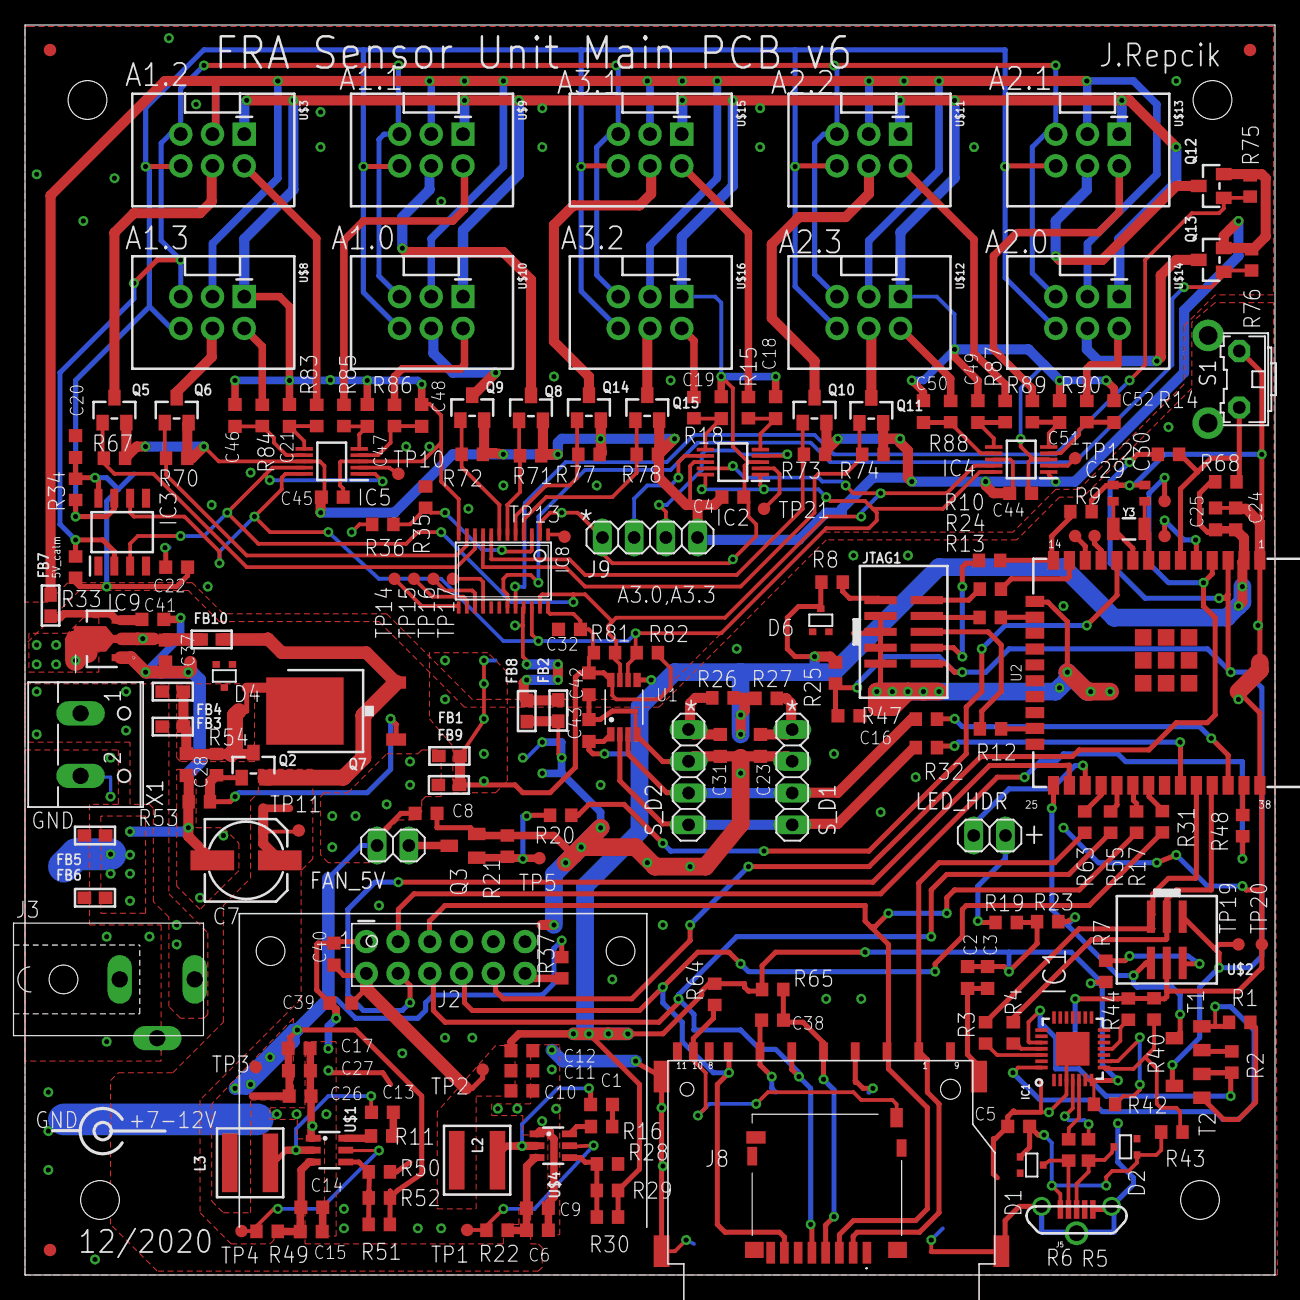
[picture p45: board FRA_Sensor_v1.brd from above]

Board: 2 copper layers, 100.0 x 100.0 mm, 214 parts (1 on the bottom side), 138 nets.

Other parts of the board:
DRILEGEND: DRILEGEND

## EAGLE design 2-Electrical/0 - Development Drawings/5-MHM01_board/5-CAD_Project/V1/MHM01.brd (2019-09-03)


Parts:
C1, C2: 10u; C1206; PARTNO JMF316AB7106KLHT
C3: 1u; C0603K; PARTNO GRM188R71C105KE15D
C5: 10u; C0603K; PARTNO GRM188R61A106KE69J
C7: 100n; C0603K; PARTNO CC0603KRX7R8BB104
FB1: FERRITE; 0603; PARTNO BLM18PG121SN1D
FID1, FID2, FID4: FIDUCIAL""; FIDUCIAL_1MM
LED2: Red; CHIPLED_1206; PARTNO BR1101W-TR
PS1: AP2202K-ADJTRG1; SOT95P280X145-5N; PARTNO AP2202K-ADJTRG1
Q1: Si2300DS; SOT23; PARTNO JMF316AB7106KLHT
R1, R7, R20, R21: 75; R1206; PARTNO CRCW120675R0FKEA
R2, R8: 10k; R0603; PARTNO CRCW060310K0FKEA
R3: 3k; R0603; PARTNO ERA-3AEB302V
R4: 0; R1206; PARTNO CRCW12060000Z0EA
R9: 220; R0603; PARTNO CRCW0603220RFKEA
R12: 100; RJ9W; PARTNO 3296X-1-101LF
R19: DNI; R1206
R22: 10K; R1206; PARTNO CRCW120610K0FKEA
TP1, TP2, TP6, TP7: TPTP10R; TP10R
U2: FIGARO_SR-7; FIGARO-SR7; PARTNO SR-7
U$1: CONN_03X2_WE_61200621621; WE_61200621621; PARTNO 61200621621
X1, X2, X3: TB001-500-02BE; W237-102; PARTNO TB001-500-02BE

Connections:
3V19: C1.1, C5.1, C7.1, PS1.5 (VOUT), R1.2, R9.1, R12.E, R12.S, R19.2, R21.2, TP7.TP, X3.2
5V: C2.1, FB1.2, U$1.4, X3.1
5V_CALM: U$1.3
ENABLE: R7.2, R22.1, X2.1
GND: C1.2, C2.2, C3.2, C5.2, C7.2, LED2.C, PS1.2 (GND), Q1.2 (S), R2.2, R4.1, R8.2, R20.1, R22.2, U$1.1, X2.2
unnamed: LED2.A, R1.1
unnamed: PS1.4 (ADJ), R2.1, R3.2, R8.1
unnamed: C3.1, FB1.1, PS1.1 (VIN), PS1.3 (EN)
unnamed: Q1.3 (D), R4.2, U2.1
unnamed: R3.1, R9.2
unnamed: Q1.1 (G), R7.1, TP6.TP
OUT_NEG: R21.1, TP2.TP, U2.4, U$1.2, X1.2
OUT_POS: R12.A, R19.1, R20.2, TP1.TP, X1.1
SCL: U$1.6
SDA: U$1.5

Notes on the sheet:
MHM01 fists to ST-7 as follows: SR7 pin MHM01 pin Function 1 2 sensor - 2 NC 3 NC 4 1 sensor+
VOUT=1.25* (1+RB/RA)
JMF316AB7106KLHT
3296X-1-101LF
V_IL = 0.5V V_IH = 1.5V V_max = 10V


Board: 2 copper layers, 33.0 x 40.0 mm, 33 parts (0 on the bottom side), 12 nets.

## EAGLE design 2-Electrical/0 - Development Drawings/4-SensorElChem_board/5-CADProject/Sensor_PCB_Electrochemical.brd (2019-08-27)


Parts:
C1: DNI; C0603K
C2, C8, C9, C12: 100n; C0603K; PARTNO GRM188R71C104KA01D
FB9: FERRITE; 0603; PARTNO BLM18PG121SN1D
FID3, FID5, FID6, FID7, FID8, FID9: FIDUCIAL1X1UNMASKED; FIDUCIAL_1MM_UNMASKED
IC4: LMP91000SD_NOPB; SON50P400X400X80-15N; PARTNO LMP91000
IC5: REF3125AQDBZRQ1; SOT95P237X112-3N; PARTNO REF3125AQDBZRQ1
J1: CONN_03X2_WE_61200621621; WE_61200621621; PARTNO 30306-6002HB
J2: 2wire; 1X02; PARTNO TSW-102-07-G-S
JP2: JUMPER-SMT_3_NO_NO_SILK; SMT-JUMPER_3_0-NO_TRACE_NO-SILK
LED1: LEDCHIP-LED0603; CHIP-LED0603; PARTNO IN-S63AT5G
Q1: PMBFJ177,215; SOT95P230X110-3N; PARTNO PMBFJ177,215
R12: 10; R0603; PARTNO CRCW060310R0FKEA
R20, R21: 10k; R0603; PARTNO CRCW060310K0FKEA
R22: 0; R0603; PARTNO CRCW06030000Z0EA
R24: 100; R0603; PARTNO CRCW0603100RFKEA
U2: TGS5042; PARTNO INSTALLED_BY_CUSTOMER
X1: 3-ELECTRODE-GAS-SENSOR_SOCKET; 3-ELE_SOCKET_ANDON; PARTNO INSTALLED_BY_CUSTOMER

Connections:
5V: IC4.2 (MENB), J1.4, R21.2, R24.1
5V_CALM: C2.1, C12.2, IC4.6 (VDD), IC5.1 (IN), J1.3, R20.1
AGND: C8.2, C9.2, C12.1, FB9.2, IC4.7 (AGND), IC4.15 (DAP), IC5.3 (GND)
CE: IC4.14 (CE), J2.1, JP2.3, X1.C (R)
GND: C2.2, FB9.1, IC4.1 (DGND), J1.1, LED1.C, R21.1
unnamed: LED1.A, R24.2
unnamed: C1.1, IC4.10 (C1)
unnamed: IC4.8 (VOUT), R12.2
unnamed: C1.2, IC4.9 (C2)
unnamed: Q1.3 (G), R20.2
RE: IC4.13 (RE), J2.2, JP2.2, Q1.2 (S), R22.1, X1.R (C)
RE_CO: JP2.1, R22.2, U2.P$2 (CE), U2.P$3 (CE)
SCL: IC4.3 (SCL), J1.6
SDA: IC4.4 (SDA), J1.5
VOUT: C9.1, J1.2, R12.1
VREF: C8.1, IC4.11 (VREF), IC5.2 (OUT)
WE: IC4.12 (WE), Q1.1 (D), U2.P$1 (WE), X1.W



Board: 2 copper layers, 55.0 x 22.0 mm, 27 parts (5 on the bottom side), 17 nets.

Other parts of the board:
DRILEGEND: DRILEGEND

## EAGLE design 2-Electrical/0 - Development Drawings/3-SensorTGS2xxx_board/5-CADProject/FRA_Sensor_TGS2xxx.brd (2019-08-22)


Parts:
C1, C2, C3: 100n; C0603K; PARTNO GRM188R71C104KA01D
C9, C10, C13: 1n; C0603K; PARTNO GRM188R71H102KA01D
FB1, FB9: FERRITE; 0603; PARTNO BLM18PG121SN1D
FID1, FID2, FID4: FIDUCIAL""; FIDUCIAL_1MM
IC3: LMV796MF_NOPB; SOT95P280X145-5N; PARTNO LMV796MF
IC6: MCP6541T-I_OT; SOT95P270X145-5N; PARTNO MCP6541T-I/OT
J1: CONN_03X2; WE_61200621621; PARTNO 30306-6002HB
Q3: Si2300DS; SOT23; PARTNO SI2300DS-T1-GE3
R1, R25, R27: 100k; R0603; PARTNO CRCW0603100KFKEA
R2, R3, R13, R23: 0; R0603; PARTNO CRCW06030000Z0EA
R4, R26: 5.1k; R0603; PARTNO CRCW06035K10FKEA
R10, R11: 10; R0603; PARTNO CRCW060310R0FKEA
R19: 10k; R0603; PARTNO CRCW060310K0FKEA
U2: FIGARO_SR-7; FIGARO-SR7; PARTNO installed_by_customer

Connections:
5V: C3.1, IC6.5 (VDD), J1.4, R2.1, R3.1, R26.1
5V_CALM: C2.1, FB1.2, IC3.5 (V+), J1.3
AGND: C1.2, C9.2, C13.2, FB9.2, IC3.2 (V-), Q3.2 (S), R1.2, R23.2
AMO_CTRL: IC6.1 (OUT), R1.1, R19.2
GAS_2: C1.1, R4.1, R10.1, U2.2
GAS_3: FB1.1, R3.2, U2.3
GAS_4: R2.2, R13.2, U2.4
GND: C2.2, C3.2, C10.2, FB9.1, IC6.2 (VSS), J1.1, R27.2, U2.1
unnamed: IC3.1 (OUTPUT), IC3.4 (-IN), R11.1
unnamed: C13.1, Q3.1 (G), R19.1
unnamed: IC3.3 (+IN), R13.1
unnamed: Q3.3 (D), R4.2, R23.1
unnamed: C10.1, IC6.4 (VIN-), R25.2
unnamed: IC6.3 (VIN+), R26.2, R27.1
SCL: J1.6
SDA: J1.5, R25.1
VOUT: C9.1, J1.2, R10.2, R11.2

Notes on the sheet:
100fA input current
inserted normally: TGS2611 TGS2612 TGS2620 TGS2444
Put SDA low for longer >1ms to activate Q3
MG-812 insetred with tab to pin3 TGS4161 inserted with tab between 2 and 3 pins
Assembled for all
R4 and R23 0R for MG-812


Board: 2 copper layers, 20.0 x 30.0 mm, 29 parts (1 on the bottom side), 16 nets.

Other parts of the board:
DRILEGEND: DRILEGEND

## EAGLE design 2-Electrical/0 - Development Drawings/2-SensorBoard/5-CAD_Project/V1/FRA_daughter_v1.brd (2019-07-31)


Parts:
C1, C2, C4, C7, C8, C9, C11, C12: 100n; C0603K
C3: 1u; C0603K
C5: 10u; C0603K
C6: DNI; C0603K
C10: 1n; C0603K
FB1, FB9: FERRITE; 0603; PARTNO BLM18PG121SN1D
FID1, FID2, FID4: FIDUCIAL""; FIDUCIAL_1MM
IC1: LMV611; SC70-5L
IC3: LMV796MF_NOPB; SOT95P280X145-5N
IC4: LMP91000SD_NOPB; SON50P400X400X80-15N
IC5: REF3125AQDBZRQ1; SOT95P237X112-3N
IC6: MCP6541T-I_OT; SOT95P270X145-5N
J1, J6, J7, J8, J9: INSERT_MM5_06691.5MM; INSERT_1MM5_9372
J2: TGS3; INSERT_MM5_0669
J3: TGS2; INSERT_MM5_0669
J4: TGS1; INSERT_MM5_0669
J5: TGS4; INSERT_MM5_0669
J10: 2wire; 1X02; PARTNO TSW-102-07-G-S
LED1: LEDCHIP-LED0603; CHIP-LED0603
PS1: AP2202K-ADJTRG1; SOT95P280X145-5N
Q1: PMBFJ177,215; SOT95P230X110-3N
Q3: Si2300DS; SOT23
R1, R25, R27: 100k; R0603
R2: 12k; R0603
R3: 5k; R0603
R4: 5.1k; R0603
R5, R6, R7, R8, R20, R21, R26: 10k; R0603
R9, R10, R11, R12: 10; R0603
R13, R14, R15, R16, R17, R18, R22, R23: 0; R0603
R24: 100; R0603
S$1: FIGARO_2611WITH_INSERTS; TH4_TGS2611_INSERTS
S$3: CITIPEL_4P50INSERTS; TH3_4P50_INSERTS
U$1: CONN_03X2_WE_61200621621; WE_61200621621
U$2: TGS5042
X1: 3-ELECTRODE-GAS-SENSORINS; 3-ELECTRODE_INSETRS

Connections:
4P25: C5.1, C7.1, J6.1, PS1.5 (VOUT), R3.1, S$3.V_POS
5V: C3.1, C11.1, IC4.2 (MENB), IC6.5 (VDD), PS1.1 (VIN), PS1.3 (EN), R15.2, R17.1, R21.2, R24.1, R26.1, U$1.4
5V_CALM: C2.1, C4.2, C12.2, FB1.2, IC1.5 (V+), IC3.5 (V+), IC4.6 (VDD), IC5.1 (IN), R6.1, R20.1, U$1.3
AGND: C1.2, C4.1, C8.2, C9.2, C12.1, FB9.2, IC1.2 (V-), IC3.2 (V-), IC4.7 (AGND), IC4.15 (DAP), IC5.3 (GND), Q3.2 (S), R1.2, R5.2, R23.2
AMO_CTRL: IC6.1 (OUT), Q3.1 (G), R1.1
CE: IC4.14 (CE), J9.1, J10.1, R22.1, X1.C
GND: C2.2, C3.2, C5.2, C6.2, C7.2, C10.2, C11.2, FB9.1, IC4.1 (DGND), IC6.2 (VSS), J1.1, LED1.C, PS1.2 (GND), R2.2, R14.1, R16.1, R18.1, R21.1, R27.2, S$3.V_NEG, U$1.1
unnamed: LED1.A, R24.2
unnamed: C6.1, PS1.4 (ADJ), R2.1, R3.2
unnamed: IC4.8 (VOUT), R12.2
unnamed: IC1.1 (+IN), R5.1, R6.2
unnamed: IC1.3 (-IN), R7.2, R8.1
unnamed: IC1.4 (OUT), R8.2, R9.1
unnamed: IC3.1 (OUTPUT), IC3.4 (-IN), R11.1
unnamed: Q1.3 (G), R20.2
unnamed: IC3.3 (+IN), R13.1
unnamed: Q3.3 (D), R4.2, R23.1
unnamed: R22.2, U$2.P$2 (CE), U$2.P$3 (CE)
unnamed: C10.1, IC6.4 (VIN-), R25.2
unnamed: IC6.3 (VIN+), R26.2, R27.1
OUT4P50_WE: IC4.12 (WE), J7.1, Q1.1 (D), R7.1, S$3.OUT, U$2.P$1 (WE), X1.W
RE: IC4.13 (RE), J8.1, J10.2, Q1.2 (S), X1.R
SCL: IC4.3 (SCL), U$1.6
SDA: IC4.4 (SDA), R25.1, U$1.5
TGS1: J4.1, R14.2, R17.2, S$1.1 (1_RH)
TGS2: C1.1, J3.1, R4.1, R10.1, R13.2, S$1.2 (2_RS_N)
TGS3: FB1.1, J2.1, R16.2, S$1.3 (3_RS_P)
TGS4: J5.1, R15.1, R18.2, S$1.4 (4_RH)
VOUT: C9.1, R9.2, R10.2, R11.2, R12.1, U$1.2
VREF: C8.1, IC4.11 (VREF), IC5.2 (OUT)

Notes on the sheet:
100fA input current
2,1V on air sensing gas, drop to 1,8V or less
TGS2611 TGS2612 TGS2620
Put SDA low for longer >1ms to activate Q3



Board: 2 copper layers, 75.0 x 40.0 mm, 67 parts (7 on the bottom side), 30 nets.

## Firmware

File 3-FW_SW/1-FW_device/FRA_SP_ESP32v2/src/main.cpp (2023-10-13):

// FRA main board source code
// Main pheripherals: ADCs, SD card, IO expander, Ethernet module
// License: GPLv2

#include "main.h"

//For Ethernet
#include <EtherCard.h>
#include <IPAddress.h>

//For time
#include <Time.h>
#include <TimeLib.h>

// Writer to SD card
#include <SPI.h>
#include "SdFat.h" //JR all SysCall::halt(); commented so the system will not go off
#include "sdios.h"
#include "FreeStack.h"

//reset fix
#include <esp_int_wdt.h>
#include <esp_task_wdt.h>

//custom pins
#define PIN_ETH_INT 36 //was 2, changed due to FW loading problems
#define PIN_ETH_NRST 4
#define PIN_LED 16
#define PIN_SD_CS  17  // SD chip select pin
#define PIN_SDA 21
#define PIN_SCL 22
#define PIN_ETH_CS 23
#define PIN_FAN 25
#define PIN_TP8 26 //used as fake SDA for real SDA line manipulation
#define PIN_TP9 27
#define PIN_BTN1 34
#define PIN_TP7 36
#define PIN_TP6 39
//custom parameters
#define ANNOUNCEMENTS_PERIOD 2000 //in ms
#define LMP91000_ADR 0x48 //checked with scanner
#define FW_VERSION "V2.0"
/*
V2.1 changelog
* add support for NDIR sensor
V2.0 changelog
* updated configuration list 
* A3.2 power enabled by default (ammonia sensor is obsolete, now poert used for NDIR module and T+RH sensor power)
V1.91 changelog
*defined framework and libraries version
V1.9 changelog
*configuration sets adjusted - added set 8 (10x H2 sensor)
V1.8 changelog
*confuguration set 7 added (4xO2 sensor on all A1 ports)
V1.7 changelog
Button can now start and stop measurement (before only start was possible)
Static IP will be used if button pressed at least 1s on DHCP wait time and after wait time.
V1.6 changelog
SDFat lib dependency fixed in project - now included in the project, EEPROM init failed and was skipped, test ok
V1.5 changelog
changed A1.3 REFCN register, fixed bug on conf set 5 and 6 (0x04 instead of 0x40)
V1.4 changelog
added configuration set 6
V1.2 changelog
*LMP registers readback and error report
*configuration sets adjusted
*/

//GPIO expander
#include <Wire.h>
#define IOEXP_ADDR 0x20 //0x75 debug board, 0x20 final

#include "Adafruit_VEML7700.h"
Adafruit_VEML7700 veml = Adafruit_VEML7700();
#include "Adafruit_Si7021.h"
Adafruit_Si7021 Si7021 = Adafruit_Si7021();

//ADC
#include "ADS1115.h"

//LMP91000 settings
#include "LMP91000conf.h"

//NDIR module custom lib
#include "NDIR_module.h"

//debug functions
//#define DEBUG_FX_ACTIVE
#ifdef DEBUG_FX_ACTIVE
  #include "debug_fx.h"
#endif

ADS1115 adc1(ADS1115_ADDRESS_ADDR_SDA);//change on V4, was GND
ADS1115 adc2(ADS1115_ADDRESS_ADDR_VDD);
ADS1115 adc3(ADS1115_ADDRESS_ADDR_SCL);

// Writer to SD card
// file system object
SdFat sd;
// text file for logging
ofstream logfile;
// buffer to format data - makes it eaiser to echo to Serial / inherited
char SDbuf[300];//limited to 299 characters
// store error strings in flash to save RAM
#define error(s) sd.errorHalt(F(s))

//For Ethernet
// ethernet mac address - must be unique on your network
uint8_t chipid[6];
byte Ethernet::buffer[500]; // tcp/ip send and receive buffer
//UDP sender
const int dstPort PROGMEM = 65511;
const int srcPort PROGMEM = 65500;
uint8_t destIp[] = { 192,168,0,255 }; // UDP unicast or broadcast, this ip does not matter, will be broadcast on given IP network by DHCP
uint8_t sendUDP_Buffer[100]; //send function limited to 220
uint8_t sendUDP_len; //length of data is going always along the array
uint8_t receiveUDP_Buffer[100]; 
uint8_t error_code[50]; //error flag, 0 at index 0 means no error

//Globals
bool use_sd=1;
bool use_veml=1;//light sensor VEML7700
bool use_Si7021=1;//Temperature and RH sensor
bool use_NDIR_module=1;//Temperature and RH sensor
bool UDP_read_flag = 0;
bool BTN1_flag = 0;
uint8_t LMPreg_TIACN = 0x00;
uint8_t LMPreg_REFCN = 0x00;
uint8_t LMPreg_MODECN = 0x02;
//functions
uint8_t sd_create_file();
uint8_t sd_format_header(uint32_t adc_period_ms);
uint8_t sd_write_sample(uint32_t sample_num);
uint8_t ioexp_init(uint8_t port1,uint8_t port2);
uint8_t ioexp_out_set(uint8_t port0,uint8_t port1);
uint8_t adc_init();
void udpReceiveProcess(uint16_t dest_port, uint8_t src_ip[IP_LEN], uint16_t src_port, const char *data, uint16_t len);
uint8_t setup_time();
void insert_to_send_buffer_header(uint32_t val);
uint8_t ioexp_read(uint8_t *port0,uint8_t *port1);
void IRAM_ATTR ISR_BTN1(){BTN1_flag = 1;}
void log_error_code(uint8_t ec);
void hard_restart();
uint8_t adc_PGA_autorange(uint8_t old_PGA,int16_t last_reading);
uint8_t ioexp_out_set_AIport(uint8_t AIport, bool statepin);
uint8_t is_sensor_out_signed(uint8_t sensor_type);
void LMP91000_setup(uint8_t configuration_set);
float SdFreeSpace();

void setup(){
  error_code[0] = 0;
  pinMode(PIN_BTN1,INPUT);
  attachInterrupt(digitalPinToInterrupt(PIN_BTN1), ISR_BTN1, FALLING);
  pinMode(PIN_ETH_INT,INPUT);
  pinMode(PIN_ETH_NRST,OUTPUT);
  digitalWrite(PIN_ETH_NRST,0);
  pinMode(PIN_LED,OUTPUT); //LED on final HW
  Serial.begin(115200);
  Serial.println(F("\n[backSoon]"));
  delay(20);
  digitalWrite(PIN_ETH_NRST,1);
  delay(10);
  Serial.printf("FW version: %s\n",FW_VERSION);

  esp_efuse_read_mac(chipid);
  chipid[5]++; //use MAC address for ETH one larger than WiFi MAC (WiFi MAC is chip ID)
  // Change 'SS' to your Slave Select pin, if you arn't using the default pin
  if (ether.begin(sizeof Ethernet::buffer, chipid, PIN_ETH_CS) == 0){
    Serial.println(F("Failed to access Ethernet controller"));
    log_error_code(1);
  }

  if (error_code[0]==0){
    Serial.println(F("Waiting for DHCP...")); //60s timeout
    if (!ether.dhcpSetup()){ //blocking, will wait for DHCP. 
    //if button was pressed in 60s wait time at least for 1s,
    //waiting will be cancelled and static ip
    //will be used (192.168.1.200,gw .1)
    //if 60s period passes, static will be set.
      Serial.println(F("DHCP failed, using static"));
      static byte smyip[] = { 192,168,5,200 };
      static byte sgwip[] = { 192,168,5,1 };
      static byte sdns[] = { 192,168,5,1 };
      static byte smask[] = { 255,255,255,0 };
      ether.staticSetup(smyip, sgwip,sdns,smask);
      //for static connection to computer CROSSOVER cable have to be used.
      log_error_code(2);
    }
  }

  Serial.printf("ETH  MAC: %02x:%02x:%02x:%02x:%02x:%02x\n",chipid[0], chipid[1], chipid[2], chipid[3], chipid[4], chipid[5]);
  chipid[5]--;
  Serial.printf("WiFi MAC: %02x:%02x:%02x:%02x:%02x:%02x\n",chipid[0], chipid[1], chipid[2], chipid[3], chipid[4], chipid[5]);
  ether.printIp("IP:  ", ether.myip);
  ether.printIp("GW:  ", ether.gwip);
  ether.printIp("DNS: ", ether.dnsip);
  for (int r=0;r<3;r++)
    destIp[r] = ether.gwip[r];
  destIp[3]=255; //broadcast address
  ether.printIp("Destination IP default: ", destIp);//Destination IP for sender
  //register udpReceiveProcess() to port 65500
  ether.udpServerListenOnPort(&udpReceiveProcess, srcPort);

  // Initialize at the highest speed supported by the board that is
  // not over 50 MHz. Try a lower speed if SPI errors occur.
  use_sd = 1;
  if (!sd.begin(PIN_SD_CS, SD_SCK_MHZ(20))) {  //SPI clock , 50MHz or 40M does not wrok, 20M ok, 
    sd.initErrorHalt(); //halt turned off, but will give logs to serial
    use_sd=0;
    log_error_code(3);
  }

  //debug_sd_log(use_sd);

  if(!Wire.begin(PIN_SDA,PIN_SCL,400000UL))
    log_error_code(4);
  
  if (!ioexp_init(0x00,0x3F)){ //unrouted expander outputs low, used low (5V on)
    error("failed to init GPIO expander");
    log_error_code(5);
  } else {
    uint8_t port0_check;
    uint8_t port1_check;
    ioexp_read(&port0_check,&port1_check);
    if (!((port0_check == 0x00)&&(port1_check == 0x3F))){
      log_error_code(8); //setting not matching
    }
  }
  //debug_GPIOexp();

  if(!adc_init()){
   error("failed to init ADC");
   log_error_code(6);
  }

  if (!veml.begin()) {
    log_error_code(18);
    error("VEML init error\n");
    use_veml = 0;
  }
  //if(use_veml) PRINTDEBUG("Lux,White,ALS: %f\t%f\t%d\n",veml.readLux(),veml.readWhite(),veml.readALS());
  if (!Si7021.begin()) {
    log_error_code(20);
    error("Si7021 init error\n");
    use_Si7021 = 0;
  }
  //fast check if NDIR is present
  if (NDIR_connection_check(NDIR_ADDR)) {
    log_error_code(43);
    error("NDIR module init error\n");
    use_NDIR_module = 0;
  } else {
    uint32_t start_NDIR = millis();

    //test read and error reporting
    uint16_t NDIRstatus = 0xFFFF;
    uint16_t NDIRgas = 0;
    uint16_t NDIRth = 0;
    PRINTDEBUG("Waiting for NDIR module to get first data...(max 2.5s)\n");
    for(uint8_t i=0;i<50;i++){ //50*50ms = max 2.5s
      delay(50);
      if (readNDIRRegisters(NDIR_ADDR, &NDIRstatus, &NDIRgas, &NDIRth)){
        log_error_code(43);
        error("NDIR module not found - continue without\n");
        use_NDIR_module = false;
        break;
      }
      //PRINTDEBUG("NDIR %d Status 0x%04X\n",i,NDIRstatus);
      if(NDIRstatus & 0x000E){ //0b xxxx xxxx xxxx xxxx xxxx 1110
        //not ready, continue looping.
      } else {
        //no error bit in status
        PRINTDEBUG("NDIR status is ready in %ld ms, Status 0x%04X\n",millis()-start_NDIR,NDIRstatus);
        break;
      }
    }
    //check if valid
    if(NDIRstatus == 0xFFFF && NDIRgas == 0xFFFF && NDIRth == 0xFFFF){
      log_error_code(44);
      error("NDIR module data not valid (all 0xFFFF)\n");
    }
    if(NDIRstatus & 0x0001){
      log_error_code(45);
      error("NDIR module error - common voltage off\n");
    }
    if(NDIRstatus & 0x000E){ //0b xxxx xxxx xxxx xxxx xxxx 1110
      log_error_code(46);
      error("NDIR module error - ACT or REF clipping\n");
    }
    if(NDIRstatus & 0x0010){
      log_error_code(47);
      error("NDIR module error - sensor not detected (temperature <-25 degC)\n");
    }
  }
  #ifdef DEBUG_FX_ACTIVE
    if(use_NDIR_module)debug_NDIR();
  #endif

  if (use_sd){
    float freeMB = SdFreeSpace();
    if (freeMB < 100) log_error_code(32);
    Serial.printf("Free Space on SD: %f MB\n",freeMB);
  }

}
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

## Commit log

2019-05-04 project setup, 2 sensors in library
    [FRA_Sensor_v1.brd, FRA_Sensor_v1.sch]
2019-05-04 sensor data
2019-05-05 TGS2611 integration
    [FRA_Sensor_v1.brd, FRA_Sensor_v1.sch, TGS2611_calculations_scaling.xlsx]
2019-05-06 programming interface ready
    [FRA_Sensor_v1.brd, FRA_Sensor_v1.sch]
2019-05-07 project setup esp32
2019-05-08 ESP32v2 debugger running, UDP receiving
2019-05-10 SCH update
    [Connections.xlsx, FRA_Sensor_v1.brd, FRA_Sensor_v1.sch]
2019-05-12 power circuits
    [FRA_Sensor_v1.brd, FRA_Sensor_v1.sch]
2019-05-14 UDP sender done
    [Connections_Ports_Memory_spec.xlsx]
2019-05-18 SD card connected
    [FRA_Sensor_v1.brd, FRA_Sensor_v1.sch]
2019-05-22 dev and sd
    mac address changed
    other sample testing
    sd card example setup
    [FRA_Sensor_v1.brd, FRA_Sensor_v1.sch]
2019-05-24 SD card logging test working
    SPI speed had to be decreased
    [Connections_Ports_Memory_spec.xlsx]
2019-05-24 placment drafts
    [FRA_Sensor_v1.brd, FRA_Sensor_v1.sch]
2019-05-25 write time analysis
    [Connections_Ports_Memory_spec.xlsx]
2019-05-25 digital sensors interface
    [FRA_Sensor_v1.brd, FRA_Sensor_v1.sch]
2019-05-26 VI and esp communication
    [Connections_Ports_Memory_spec.xlsx]
2019-05-28 labview ACKs
    [Connections_Ports_Memory_spec.xlsx]
2019-06-04 sch and layiout
    [FRA_Sensor_v1.brd, FRA_Sensor_v1.sch]
2019-06-04 jtag layout
    [FRA_Sensor_v1.brd, FRA_Sensor_v1.sch]
2019-06-05 power layouts
    [FRA_Sensor_v1.brd, FRA_Sensor_v1.sch]
2019-06-09 sch cap miltuplier add
    [FRA_Sensor_v1.brd, FRA_Sensor_v1.sch]
2019-06-16 sensor datasheets
2019-06-19 datasheets, sch update
    [Connections_Ports_Memory_spec.xlsx, FRA_Sensor_v1.brd, FRA_Sensor_v1.sch, System_spec.xlsx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]
2019-06-24 ldo addded
    [FRA_Sensor_v1.brd, FRA_Sensor_v1.sch, System_spec.xlsx]
2019-06-27 sch update
    layout, od powerm SPIs,
    [FRA_Sensor_v1.brd, FRA_Sensor_v1.sch, System_spec.xlsx]
2019-07-12 sch update layout update
    [Cart_Jul10_0914PM.xls, FRA_Sensor_v1.brd, FRA_Sensor_v1.sch, FRA_daughter_v1.brd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]
2019-07-13 layout done,
    [FRA_Sensor_v1.brd, FRA_Sensor_v1.sch]
2019-07-17 SD and ethernet merged
    [FRA_Sensor_v1.brd, FRA_Sensor_v1.sch, System_spec.xlsx]
2019-07-18 adc integrated, 2 ADCs tested
    [AssemblyBOM.xlsx, AssemblyBOM_forALLPCB.xlsx]
2019-07-20 announcements, io expander, ...
    [System_spec.xlsx, error_codes.csv]
2019-07-24 power reports done, interrupt ethernet..
    [System_spec.xlsx, error_codes.csv]
2019-07-25 boad update v2
    [AssemblyBOM_forALLPCB.xlsx, FRA_Sensor_v1.brd, FRA_Sensor_v1.sch, PurchaseBOM_forALLPCB.xlsx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]
2019-07-25 error code array instead one value
    [System_spec.xlsx]
2019-07-26 error report fixed and sw reset done
    [FRA_Sensor_v1.brd, FRA_Sensor_v1.sch, System_spec.xlsx]
2019-07-27 fixed network, ADC begin
    [04 - MouserBom_v3.xls, All_BOMs_prepation_v1.xlsx, All_BOMs_prepation_v3.xlsx, AssemblyBOM.csv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]
2019-07-29 sch main final touches
    [FRA_Sensor_v1.sch, System_spec.xlsx]
2019-07-30 sensor board sch and layout
    [FRA_Sensor_v1.brd, FRA_daughter_v1.brd, FRA_daughter_v1.sch, Pending Sensor Selection.xlsx]
2019-07-31 BOM updates, labview
    [01Log2019_07_30-13_41_30.csv, 01Log2019_07_30-20_52_24.csv, 01Log2019_07_30-21_03_58.csv, All_BOMs_prepation_v3.1_CHINA.xlsx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]
2019-08-01 sd card logging done
    [01Log2019_07_30-13_41_30.csv, 01Log2019_07_30-20_52_24.csv, 01Log2019_07_30-21_03_58.csv, 01Log2019_07_31-21_08_56.csv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]
2019-08-02 Light sensor integrated
    [01Log2019_07_31-21_08_56.csv, 01Log2019_07_31-21_11_05.csv, 01Log2019_07_31-21_21_54.csv, 01Log2019_08_01-15_30_53.csv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]
2019-08-06 updates
    amonia sensor
    preparation for LMP91000
    ADC1 address changed to match V4 board
    [01Log2019_08_04-19_07_21.csv, 01Log2019_08_05-17_32_44.csv, 01Log2019_08_05-18_09_39.csv, 01Log2019_08_05-18_12_07.csv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]
2019-08-07 data saving fixes, ADC address changed
    [01Log2019_08_06-18_53_07.csv, System_spec_v1.xlsx]
2019-08-09 sensor board update, main VI update
    [FRA_daughter_v2.brd, FRA_daughter_v2.sch, Preliminary_sourcing_BOM_sensorPCB_v1.xlsx]
2019-08-16 hw design updates
    [64013A1_BOM_v3.2_VK_2019-08-14_FRA190515.xlsx, 64013A1_BOM_v4.1_VK_2019-08-14_FRA190515.xlsx, 64013A1_BOM_v5_VK_2019-08-14_FRA190516.xlsx, BOMs_Sensor_board_v1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]
2019-08-17 amonia sensor tuning
    [FRA_Sensor_TGS2xxx.brd, FRA_Sensor_TGS2xxx.sch]
2019-08-18 TGS board update
    [64013A1_BOM_v5_VK_2019-08-14_FRA190516.xlsx, BOMs_Sensor_board_v1.1_allVariants.xlsx, FRA_Sensor_TGS2xxx.brd, FRA_Sensor_TGS2xxx.sch]
2019-08-18 electrochemical board design
    [Sensor_PCB_Electrochemical.brd, Sensor_PCB_Electrochemical.sch]
2019-08-19 updates spec
    [System_spec_v3.xlsx]
2019-08-20 programing procedure, elchem board
    [BOMs_Sensor_board_v1.1_allVariants.xlsx, BOMs_Sensor_board_v1_allVariants.xlsx, ElChemPCB_BOMs_all_V1.xlsx, Sensor_PCB_Electrochemical.brd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]
2019-08-20 LMP code align
    [Cart_Jul10_0914PM.xls, System_spec_v3.xlsx, error_codes.csv]
2019-08-20 versioning start
    [System_spec_v3.xlsx]
2019-08-20 full SD card check
    [error_codes.csv]
2019-08-20 csv sync to git
    [Assembly_partlist_all_v1.csv, Partlist_coordinates.csv, partlist.csv, partlist_exp_v5_not_used.csv]
2019-08-21 legends fix
    [System_spec_v3.xlsx]
2019-08-22 sensor tests
    [64307A1_BOM_Sensor_board_v1_allVariants_VK_2019-08-19_FRAcomm.xlsx, 64307A1_BOM_Sensor_board_var B_allVariants_VK_2019-08-19_FRAcomm.xlsx, 64307A1_BOM_Sensor_b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]
2019-08-23 sensor elchem testing, reports, code update
    [64307A1_BOM_Sensor_board_varC_allVariants_VK_2019-08-20_FRAcomm2.xlsx, Chamber_measurements.xlsx, System_spec_v4.xlsx, error_codes.csv]
2019-08-23 electrochemical sensors test results
    [Chamber_measurements.xlsx, System_spec_v4.xlsx]
2019-08-27 data processing, orders review, tests, elchem pcb RE CE swap
    [64013A1_PBOM_2019082663413.xlsx, 64307A1_M1_OrderRelease_Sensor_board_2019-08-23.xlsx, 64307A1_M1_PBOM_Sensor_board_2019-08-23.xlsx, 64307A1_T1_OrderRelease_Se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]
2019-08-29 mhm01 board
    [MHM01.brd, MHM01.gko, MHM01.sch, System_spec_v4.xlsx]
2019-09-03 BOM updates
    [64307A1_M1_OrderRelease_Sensor_board_2019-08-23.xlsx, 64307A1_M1_PBOM_2019090260346.xlsx, 64307A1_M1_PBOM_Sensor_board_2019-08-23.xlsx, 64307A1_T1_OrderRelease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]
2019-09-07 labview miltiple unit selection
    [System_spec_v4.xlsx]
2019-09-07 update of conf. sets
    [System_spec_v4.xlsx]
2019-10-08 converter to app specific values
    [System_spec_v4.xlsx]
2019-10-29 silkscreen update
    [FRA_Sensor_v1.brd, FRA_Sensor_v1.gko]
2019-11-02 V1.4 update conf set
    [System_spec_v4.xlsx]
2019-11-23 bug fix app spec converter
    [System_spec_v4.xlsx]
2019-11-30 added sdfat, searching for issues
    [ESP32_RF_INIT.xlsx, ESP8266_RF_init.xls, ESP8266_RF_init.xlsx]
2019-11-30 CS ETH pin change
2019-12-04 button stop measurement fcn, static fallback IP, V1.7 release
    [System_spec_v4.xlsx]
2019-12-04 added pics
    [System_spec_v4.xlsx]
2019-12-06 3d export
    [System_spec_v4.xlsx]
2019-12-06 3D model created
    [FRA_Sensor_v1_SW.SLDPRT, esp32wroom.SLDPRT, fra_sensor_v1.SLDASM]
2019-12-14 ME box project setup
    [BOX_bottom.SLDPRT, BOX_top_all.SLDASM, fra_sensor_v1.SLDASM]
2020-03-04 junction board
    [FRA_junctionB_v1.brd, FRA_junctionB_v1.sch, SSW-103-01-F-D.x_b, System_spec_v4.xlsx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]
2020-03-04 manuf data junction b
    [copper_bottom.gbr, copper_top.gbr, drill_1_16.xln, gerber_job.gbrjob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]
2020-03-07 bulkhead board
    [FRA_breakout6U_v1.brd, FRA_breakout6U_v1.sch, FRA_bulkhead_v1.brd, FRA_bulkhead_v1.sch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]
2020-03-18 bulkhead design, updated confsets added 7th
    [BOM_FRA_breakout6U.xlsx, BOM_FRA_bulkhead.xlsx, FRA_bulkhead_v1.brd, FRA_bulkhead_v1.xlsx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]
2020-12-03 edited ESP32 footprint
    [FRA_Sensor_v1.brd, FRA_Sensor_v1.sch]
2020-12-03 generated gerber data
    [FRA_Sensor_v1.gko, gerber_job.gbrjob]
2020-12-04 silkscreen edits on breakout boards
    [BOM-2020-12-04.xlsx, FRA_breakout6U_v1.brd, FRA_breakout6U_v1.gko, FRA_breakout6U_v1.sch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]
2021-06-01 add sample images
2021-09-27 flash procedure updated, Labview app update
    *convert data live in preview graphs
    *make special conversions and integrations in graph D - enabled in dot tab.
    [ESP32_RF_INIT.xlsx, ESP8266_RF_init.xls, ESP8266_RF_init.xlsx]
2022-12-21 Added framework and libraries version. For new version, I2C and MAC need to be updated.
2023-08-10 New configuration for elchem. Removed amonia from FW. Updated flash guide debug. New FW release.
    [System_spec_v4.xlsx]
2023-10-13 add NDIR module support. FW code cleanup.
    [System_spec_v4.xlsx, error_codes.csv]

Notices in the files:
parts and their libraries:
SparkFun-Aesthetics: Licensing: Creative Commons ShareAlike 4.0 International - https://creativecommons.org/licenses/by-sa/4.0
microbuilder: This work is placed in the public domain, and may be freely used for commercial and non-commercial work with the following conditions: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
